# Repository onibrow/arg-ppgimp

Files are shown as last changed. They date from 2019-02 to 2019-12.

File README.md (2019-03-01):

# Arias Research Group - PPG & Impedence Measurement

## Seiya Ono Sp'19

The goal of this project is to collaborate with doctors at UCSD and Dr. Muller's student, Sina Faraji, to create a test bench for our group's Bioimpedence Array and OLED/OPD Oxymeter sensors to measure tissue damage in mice. We hope to use Sina Faraji's new OLED/OPD driver chip to take PPG measurements while using our own impedence arrays and electronics to measure tissue of the target.

-----

## Specs

- 1 PPG Sensor
    - 1 Red OLED
    - 1 NIR OLED
    - 1 OPD
    - Sina's Driver Chip
- 15 Impedence Electrodes
    - Impedence measurement AFE
    - Current Driver (200uA to 700uA, up to 1mA)
    - 15 to 2 selection mux
- 9V Power
- Coms over Serial

### PPG Sensor

Sina's OLED/OPD Driver Amplifier has the capability to driver 8 pairs of OLEDs and take readings from 8 OPDs. It handles all the amplification through SPI programmable registers. The closed loop in the transimpedence amplifiers can help get rid of any DC components in the OPD readings. It runs off of 1.1V digital logic, and 8V driver power.

If his chip does not go well, we will implement our own OLED drivers and OPD transimpedence amplifiers.

### Impedence Electrodes

We were asked to get our 15 electrode array to be able to take any impedence measurement between any two user selectable electrodes, while also being able to select any two electrodes to drive with a set amount of current. This divides this part of the board into three distance parts - the multiplexor selection and configuration, tunable current source, and impdence measurement. The following section will outline the different chip selection and their respective specs.

#### Multiplexor

Because the board is spec'd to be able to take impedence measurements as well as source current, it is critical to choose a multiplexor that has very low on resistance, while having very high off resistance. Luckily, most CMOS technology has this as standard, so picking an analog mux was not very difficult. We settled with the [ADG1608/1609](https://www.analog.com/en/products/adg1608.html) because of its 3 bit (8 input) mux, as well as its secondary variant 2 bit (4x2 input) DPDT (double pole double throw) configuration. To differentiate, the ADG1608 variant is the 3 bit 8 input mux, and the ADG1609 is the 2 bit 4x2 input mux. See the figure below for clarification.

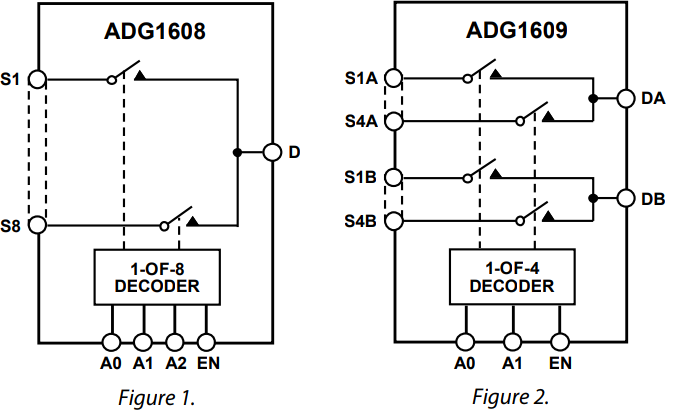
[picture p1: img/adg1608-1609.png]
mux diff


By using two pairs of ADG1608's, a 16x2 input 1x2 output can be created. This means the circuit can individually select a pair of electrodes to be used by the impedence analyzer and tunable current source. To select between either of the two inputs, the ADG1609 will be used as a demuxer to select either the impedence analyzer or tunable current source. The DPDT configuration is very usedful in this sceneario because we are trying to always drive a _pair_ of electrodes. Here are some important specs when running off of a 3.3V power rail.

| Parameter | Value | Unit |
| --------- | ----- | ---- |
| R\_on      | 13.5  | Ohms |
| S/D Leakage | 0.1 | nA max |
| -3dB 1608 | 34 | MHz typ |
| -3dB 1609 | 72 | MHz typ |
| C\_S OFF | 23 | pF typ |
| C\_D OFF 1608 | 145 | pF type |
| C\_D OFF 1609 | 72 | pF typ |
| C\_S/D ON 1608 | 173 | pF typ |
| C\_S/D ON 1609 | 95 | pF typ |
| I\_DD | 0.001 | uA typ |
| V\_DD | 3.3 | V |
|I\_S/D 1608 | 126 | mA max |
|I\_S/D 1609 | 94 | mA max |

As we are dealing with specimens in the 10K Ohm range, the 13.5 Ohm and 173pF ON impedence is negligible, even if the electrode is traveling through 2 multiplexors. The max available current draw is much over the required 1mA of current through the electrodes, so the chip fits our needs. It aslo fits our impedance chip bandwidth, where it can do frequency sweeps over 1kHz to 100kHz. More on this in the "Impedence Analyzer" section.

#### Tunable Current Source

In order to drive our selectable electrodes with a user defined amount of current, we needed an adjustable current source. For this task, the [LM134/LM234/LM334 3-Terminal Adjustable Current Source](http://www.ti.com/product/LM134) was chosen. Specifically, the LM334 was chosen for its small form factor and easily identifiable 3-Pin Through Hole casing. It has a huge operating voltage from 1V to 40V, and can be tuned to supply current between 1uA to 10mA. The chip can also be operated in a temperature compensation region to eliminate its temperature dependence up to 0.2% accuracy.

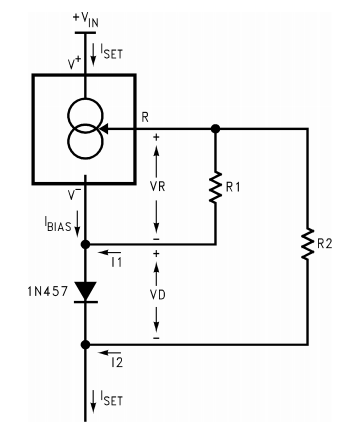
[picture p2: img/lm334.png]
LM334


For this circuit, the diode to use was already suggested, so the next choice was to pick out a digital potentiometer. TI also provided the math to prove the temperature coefficient compensation with the chosen diode, and drew the following relationship between R1 and R2:

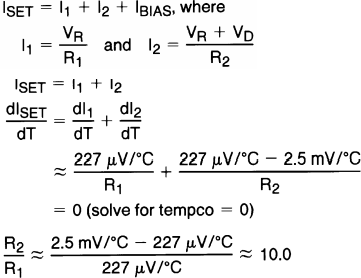
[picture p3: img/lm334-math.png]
lm334 math


From this, 1k and 10k 256 step digital potentiometers were chosen, with the math coming out to 3.9/39 Ohms per step, capable of driving in the range of 67.7uA to just short of 1mA. This just about fits our spec, going over to the upper limit of 1mA. The digital potentiometers chosen are the [AD8400](https://www.analog.com/en/products/ad8400.html) in both the 1K and 10K variant. They are controlled over SPI as designated write only slave devices. It can operate at between 3V and 5.5V and will typically draw less than 1mA.

#### Impedence Measurements

We would like to measure impedences between 1M Ohm (Magnitude) and 1k Ohm on our species. The chip for this is the [AD5933](https://www.analog.com/en/products/ad5933.html) which can do frequency sweeps. See Page 14 of the Data Sheet for more information on how to program the chip to do this.

Setting Gain - See Page 18 on how to choose the Gain setting resistor R\_FB to ensure that the analog readings do not saturate. The gain factor needs to be recalculated if R\_FB changes, if the output excitation voltage (more on this later) changes, or if the PGA gain is set differently. On the topic of operating voltages, there are 4 to choose from:

| Range | Output Excitation Voltage Amplitude | Output DC Bias Level | Output Series Resistance |
| ----- | ----------------------------------- | -------------------- | ------------------------ |
| 1 | 1.98 V p-p | 1.48 V | 200 Ohm |
| 2 | 0.97 V p-p | 0.76 V | 2.4k Ohm |
| 3 | 383 mV p-p | 0.31 V | 1.0k Ohm |
| 4 | 198 mV p-p | 0.173 V| 600 Ohm |

These numbers factor into what value should be chosen for the feedback resistor. The equation for choosing the feedback resistor is as follows:

Output Excitation Voltage Range * Gain Setting Resistor / Z\_Uknown * PGA Gain

By selecting the typical range 1 (~2V p-p) setting, we must choose a R\_FB that is roughly on the same order of magnitude as the unknown impedences we are measuring. From Yasser's Ulcer sensing paper (Swisher, S. L. et al. Impedance sensing device enables early detection of pressure ulcers in vivo. Nat. Commun. 6:6575 doi: 10.1038/ncomms7575 (2015)), we find that the typical impedence magnitude ranges from 10^4 to 10^6, so we will choos a 1M Ohm resistor for the feedback. This way, it should be able to cover a very wide range of impedences.

The chip does come with an internal 16.776 MHz oscillator, but it can be replaced by placing a 16MHz oscillator on MCLK, and then setting the control register to use the external clock. By default, on power up the internal oscillator is selected.

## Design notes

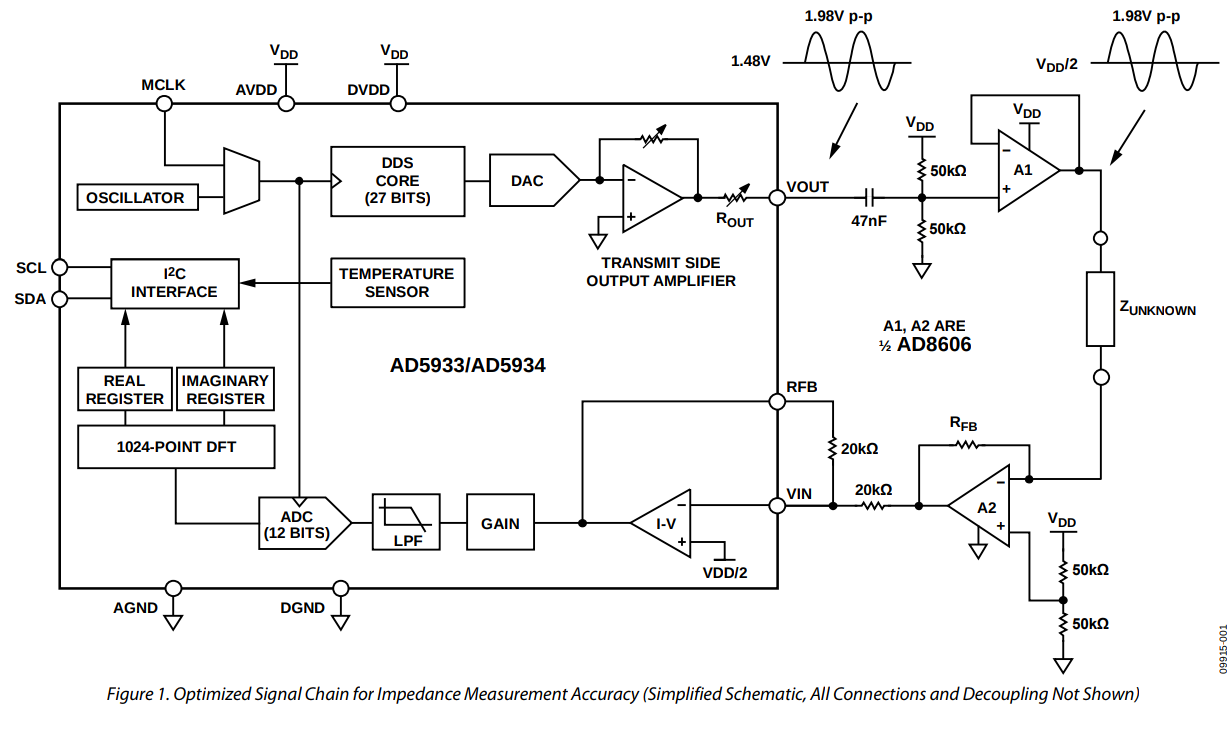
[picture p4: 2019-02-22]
img/ad5933-circ.png

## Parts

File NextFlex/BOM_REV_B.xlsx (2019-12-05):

Comment | Designator | Footprint | LCSC Part #（optional）
0.1uF | C9, C13, C14, C15 | 0603_C | C14663
1uF | C1, C2, C7, C8, C10, C11, C12 | 0603_C | C15849
18pF | C3, C4 | 0603_C | C1647
2.2uF | C5, C6 | 0603_C | C23630
10k | R1, R2, R3, R10 | 0603_R | C25804
22 | R4, R5 | 0603_R | C23345
330 | R7, R8, R11, R12, R13 | 0603_R | C23138
1k | R6, R9 | 0603_R | C21190
100k | R_CAL, R_FB | 0603_R | C25803
ATMEGA32U4 | U8 | QFN-44_EP_7x7x0.5P | C112161
Green | D3, D5 | LED_0603 | C72043
Red | D4, D7, D8, D9 | LED_0603 | C2286

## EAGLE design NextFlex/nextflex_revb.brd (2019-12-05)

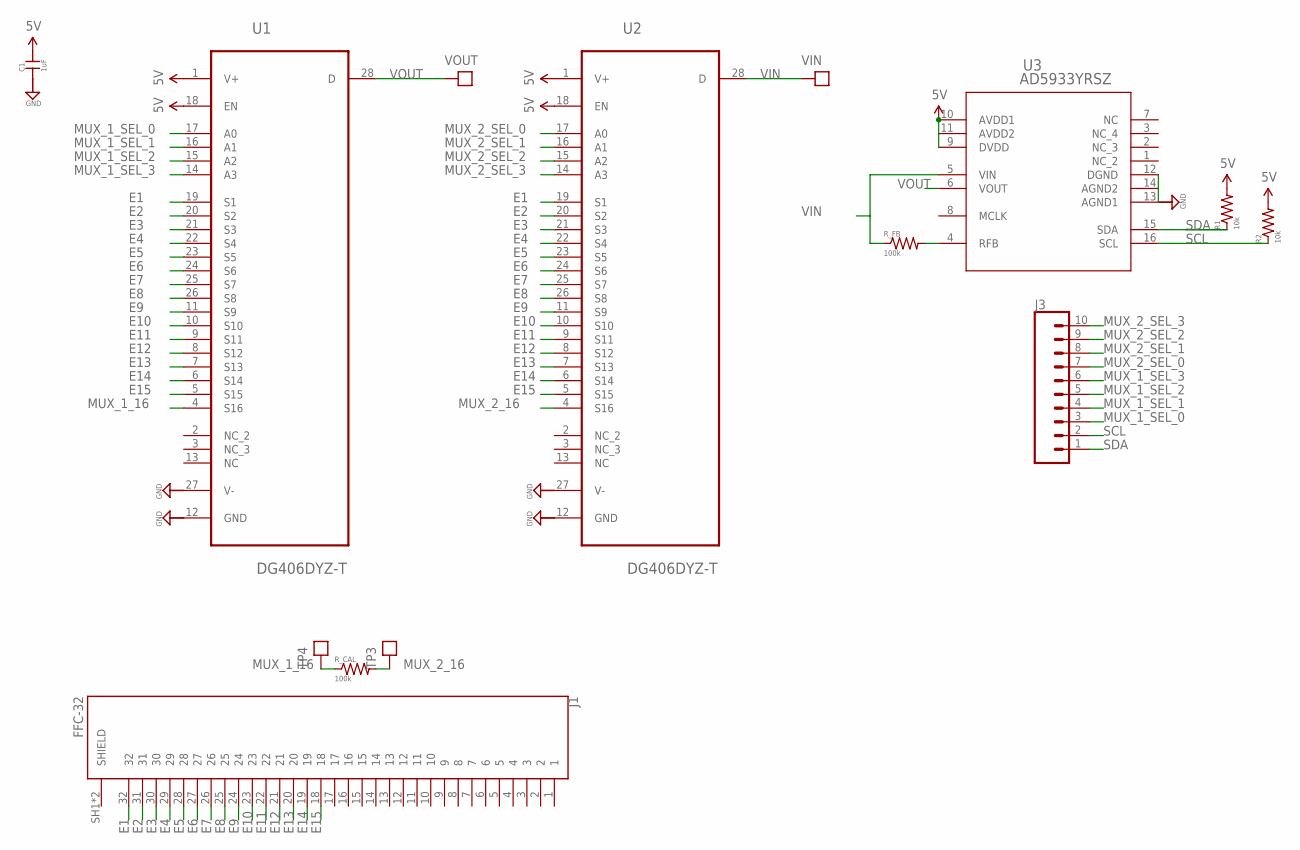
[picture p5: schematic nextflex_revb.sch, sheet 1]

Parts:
C1: 1uF; 0603-CAP
J1: FFC-32; MOLEX_503480-3200
J3: CONN_10"; 1X10
R1, R2: 10k; 0603-RES
R_CAL: 100k; 0603-RES
R_FB: 100k; 0603-RES
TP3, TP4: TEST_POINTTHRU; TEST_POINT
U1, U2: DG406DYZ-T; SOIC127P1032X265-28N
U3: AD5933YRSZ; RS_16
VIN: TEST_POINTTHRU; TEST_POINT
VOUT: TEST_POINTTHRU; TEST_POINT

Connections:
5V: C1.2, R1.2, R2.2, U1.1 (V+), U1.18 (EN), U2.1 (V+), U2.18 (EN), U3.9 (DVDD), U3.10 (AVDD1), U3.11 (AVDD2); also elsewhere on the board
E1: J1.32, U1.19 (S1), U2.19 (S1)
E2: J1.31, U1.20 (S2), U2.20 (S2)
E3: J1.30, U1.21 (S3), U2.21 (S3)
E4: J1.29, U1.22 (S4), U2.22 (S4)
E5: J1.28, U1.23 (S5), U2.23 (S5)
E6: J1.27, U1.24 (S6), U2.24 (S6)
E7: J1.26, U1.25 (S7), U2.25 (S7)
E8: J1.25, U1.26 (S8), U2.26 (S8)
E9: J1.24, U1.11 (S9), U2.11 (S9)
E10: J1.23, U1.10 (S10), U2.10 (S10)
E11: J1.22, U1.9 (S11), U2.9 (S11)
E12: J1.21, U1.8 (S12), U2.8 (S12)
E13: J1.20, U1.7 (S13), U2.7 (S13)
E14: J1.19, U1.6 (S14), U2.6 (S14)
E15: J1.18, U1.5 (S15), U2.5 (S15)
GND: C1.1, U1.12 (GND), U1.27 (V-), U2.12 (GND), U2.27 (V-), U3.12 (DGND), U3.13 (AGND1), U3.14 (AGND2); also elsewhere on the board
MUX_1_16: R_CAL.1, TP4.1, U1.4 (S16)
MUX_1_SEL_0: J3.3, U1.17 (A0); also elsewhere on the board
MUX_1_SEL_1: J3.4, U1.16 (A1); also elsewhere on the board
MUX_1_SEL_2: J3.5, U1.15 (A2); also elsewhere on the board
MUX_1_SEL_3: J3.6, U1.14 (A3); also elsewhere on the board
MUX_2_16: R_CAL.2, TP3.1, U2.4 (S16)
MUX_2_SEL_0: J3.7, U2.17 (A0); also elsewhere on the board
MUX_2_SEL_1: J3.8, U2.16 (A1); also elsewhere on the board
MUX_2_SEL_2: J3.9, U2.15 (A2); also elsewhere on the board
MUX_2_SEL_3: J3.10, U2.14 (A3); also elsewhere on the board
unnamed: R_FB.2, U3.4 (RFB)
SCL: J3.2, R2.1, U3.16 (SCL); also elsewhere on the board
SDA: J3.1, R1.1, U3.15 (SDA); also elsewhere on the board
VIN: R_FB.1, U2.28 (D), U3.5 (VIN), VIN.1
VOUT: U1.28 (D), U3.6 (VOUT), VOUT.1

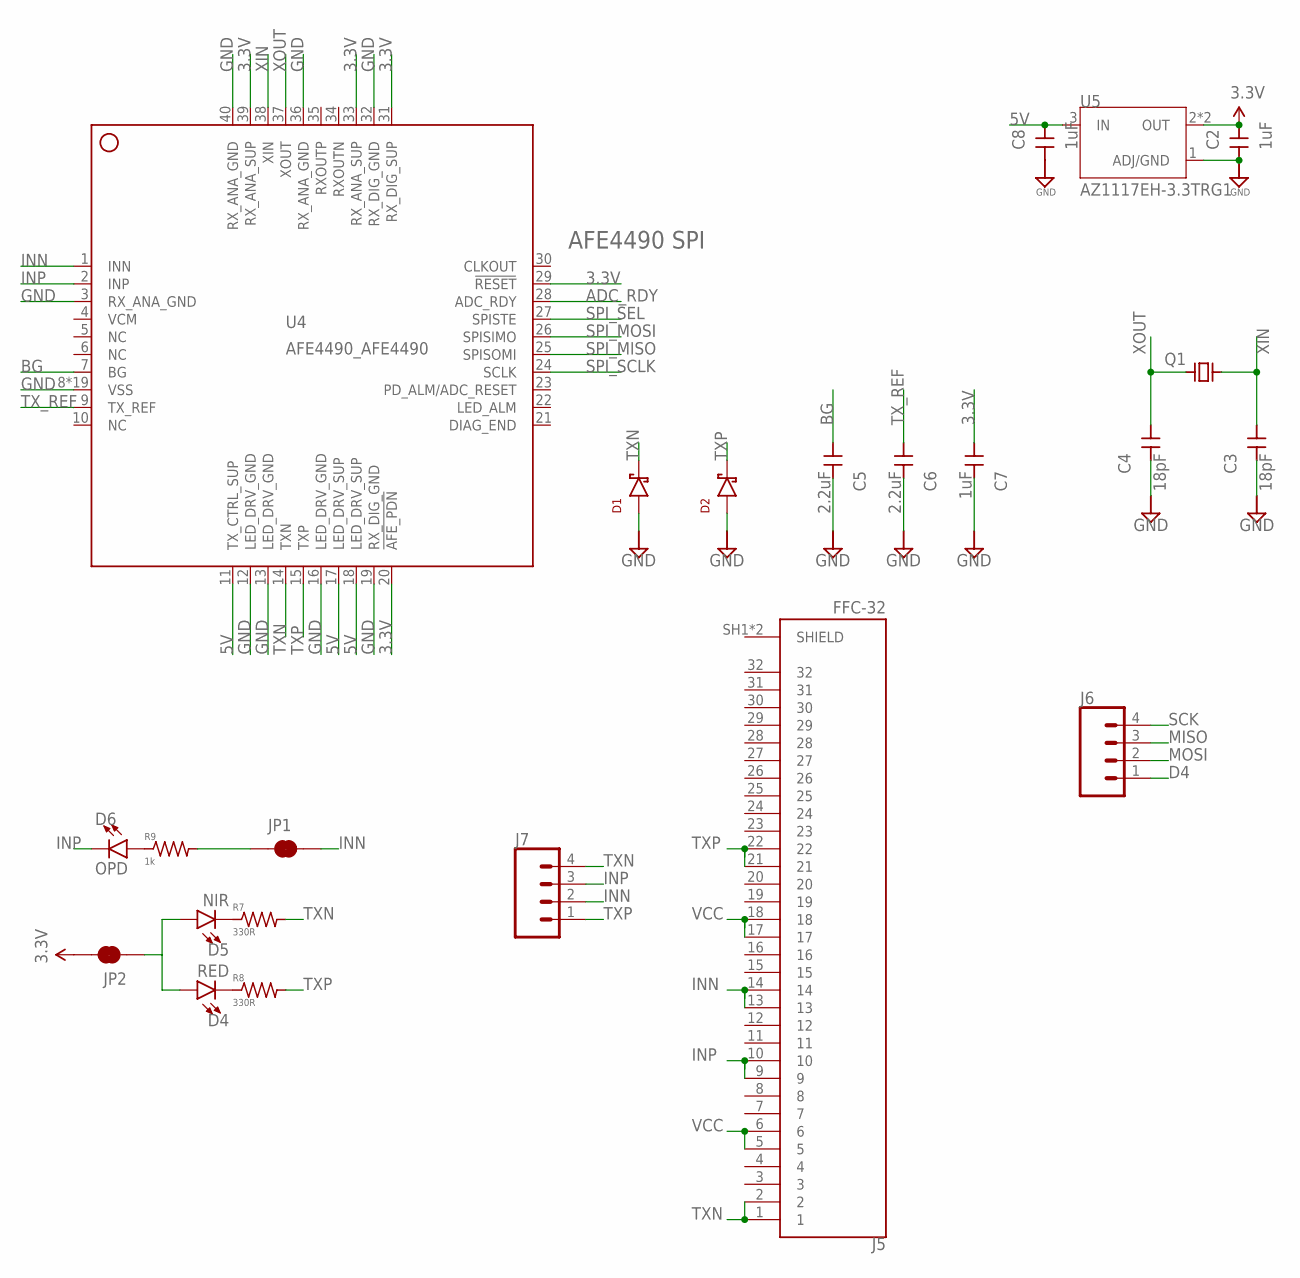
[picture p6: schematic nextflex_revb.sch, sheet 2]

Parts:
C2, C7, C8: 1uF; 0603-CAP
C3, C4: 18pF; 0603-CAP
C5, C6: 2.2uF; 0603-CAP
D1, D2: DIODE_CZRU; CZRU
D4: RED; LED-0603
D5: NIR; LED-0603
D6: OPD; LED-1206
J5: FFC-32; MOLEX_503480-3200
J6, J7: CONN_04; 1X04
JP1, JP2: JUMPER-SMT_2_NC_TRACE_NO-SILK; SMT-JUMPER_2_NC_TRACE_NO-SILK
Q1: CRYSTAL_SMOL; XTAL500X320X130N
R7, R8: 330R; 0603-RES
R9: 1k; 0603-RES
U4: AFE4490_AFE4490; AFE4490_QFN40-6X6
U5: AZ1117EH-3.3TRG1; SOT230P700X180-4N

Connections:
3.3V: C2.1, C7.1, JP2.2, U4.20 (!AFE_PDN), U4.29 (!RESET), U4.31 (RX_DIG_SUP), U4.33 (RX_ANA_SUP), U4.39 (RX_ANA_SUP), U5.2 (OUT), U5.4 (OUT); also elsewhere on the board
5V: C8.1, U4.11 (TX_CTRL_SUP), U4.17 (LED_DRV_SUP), U4.18 (LED_DRV_SUP), U5.3 (IN); also elsewhere on the board
ADC_RDY: U4.28 (ADC_RDY)
BG: C5.1, U4.7 (BG)
D4: J6.1; also elsewhere on the board
GND: C2.2, C3.2, C4.2, C5.2, C6.2, C7.2, C8.2, D1.P, D2.P, U4.3 (RX_ANA_GND), U4.8 (VSS), U4.12 (LED_DRV_GND), U4.13 (LED_DRV_GND), U4.16 (LED_DRV_GND), U4.19 (RX_DIG_GND), U4.32 (RX_DIG_GND), U4.36 (RX_ANA_GND), U4.40 (RX_ANA_GND), U4.EXP@1 (VSS), U4.EXP@2 (VSS), U4.EXP@3 (VSS), U4.EXP@4 (VSS), U4.EXP@5 (VSS), U4.EXP@6 (VSS), U4.EXP@7 (VSS), U4.EXP@8 (VSS), U4.EXP@9 (VSS), U4.EXP@10 (VSS), U4.EXP@11 (VSS), U4.EXP@12 (VSS), U4.EXP@13 (VSS), U4.EXP@14 (VSS), U4.EXP@15 (VSS), U4.EXP@16 (VSS), U4.PWR@1 (VSS), U4.PWR@2 (VSS), U5.1 (ADJ/GND); also elsewhere on the board
INN: J5.13, J5.14, J7.2, JP1.2, U4.1 (INN)
INP: D6.C, J5.9, J5.10, J7.3, U4.2 (INP)
MISO: J6.3; also elsewhere on the board
MOSI: J6.2; also elsewhere on the board
unnamed: D4.A, D5.A, JP2.1
unnamed: D5.C, R7.1
unnamed: D4.C, R8.1
unnamed: D6.A, R9.1
unnamed: JP1.1, R9.2
SCK: J6.4; also elsewhere on the board
SPI_MISO: U4.25 (SPISOMI); also elsewhere on the board
SPI_MOSI: U4.26 (SPISIMO); also elsewhere on the board
SPI_SCLK: U4.24 (SCLK); also elsewhere on the board
SPI_SEL: U4.27 (SPISTE); also elsewhere on the board
TXN: D1.N, J5.1, J5.2, J7.4, R7.2, U4.14 (TXN)
TXP: D2.N, J5.21, J5.22, J7.1, R8.2, U4.15 (TXP)
TX_REF: C6.1, U4.9 (TX_REF)
VCC: J5.5, J5.6, J5.17, J5.18; also elsewhere on the board
XIN: C3.1, Q1.1 (A), U4.38 (XIN)
XOUT: C4.1, Q1.2 (B), U4.37 (XOUT)

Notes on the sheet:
AFE4490 SPI

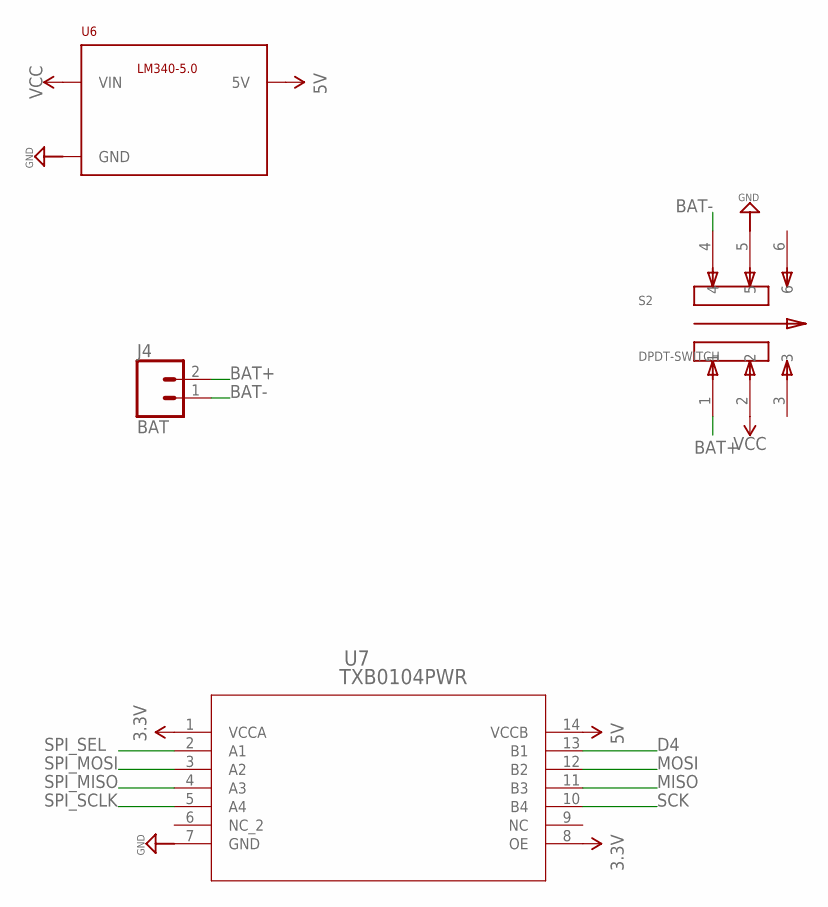
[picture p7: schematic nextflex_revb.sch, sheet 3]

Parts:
J4: BAT; 1X02
S2: DPDT-SWITCH; SW_JS202011SCQN
U6: LM340MPX-5.0230; SOT230P700X180-4N
U7: TXB0104PWR; PW14

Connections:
3.3V: U7.1 (VCCA), U7.8 (OE); also elsewhere on the board
5V: U6.3 (5V), U7.14 (VCCB); also elsewhere on the board
BAT+: J4.2, S2.1
BAT-: J4.1, S2.4
D4: U7.13 (B1); also elsewhere on the board
GND: S2.5, U6.2 (GND), U6.4 (GND), U7.7 (GND); also elsewhere on the board
MISO: U7.11 (B3); also elsewhere on the board
MOSI: U7.12 (B2); also elsewhere on the board
SCK: U7.10 (B4); also elsewhere on the board
SPI_MISO: U7.4 (A3); also elsewhere on the board
SPI_MOSI: U7.3 (A2); also elsewhere on the board
SPI_SCLK: U7.5 (A4); also elsewhere on the board
SPI_SEL: U7.2 (A1); also elsewhere on the board
VCC: S2.2, U6.1 (VIN); also elsewhere on the board

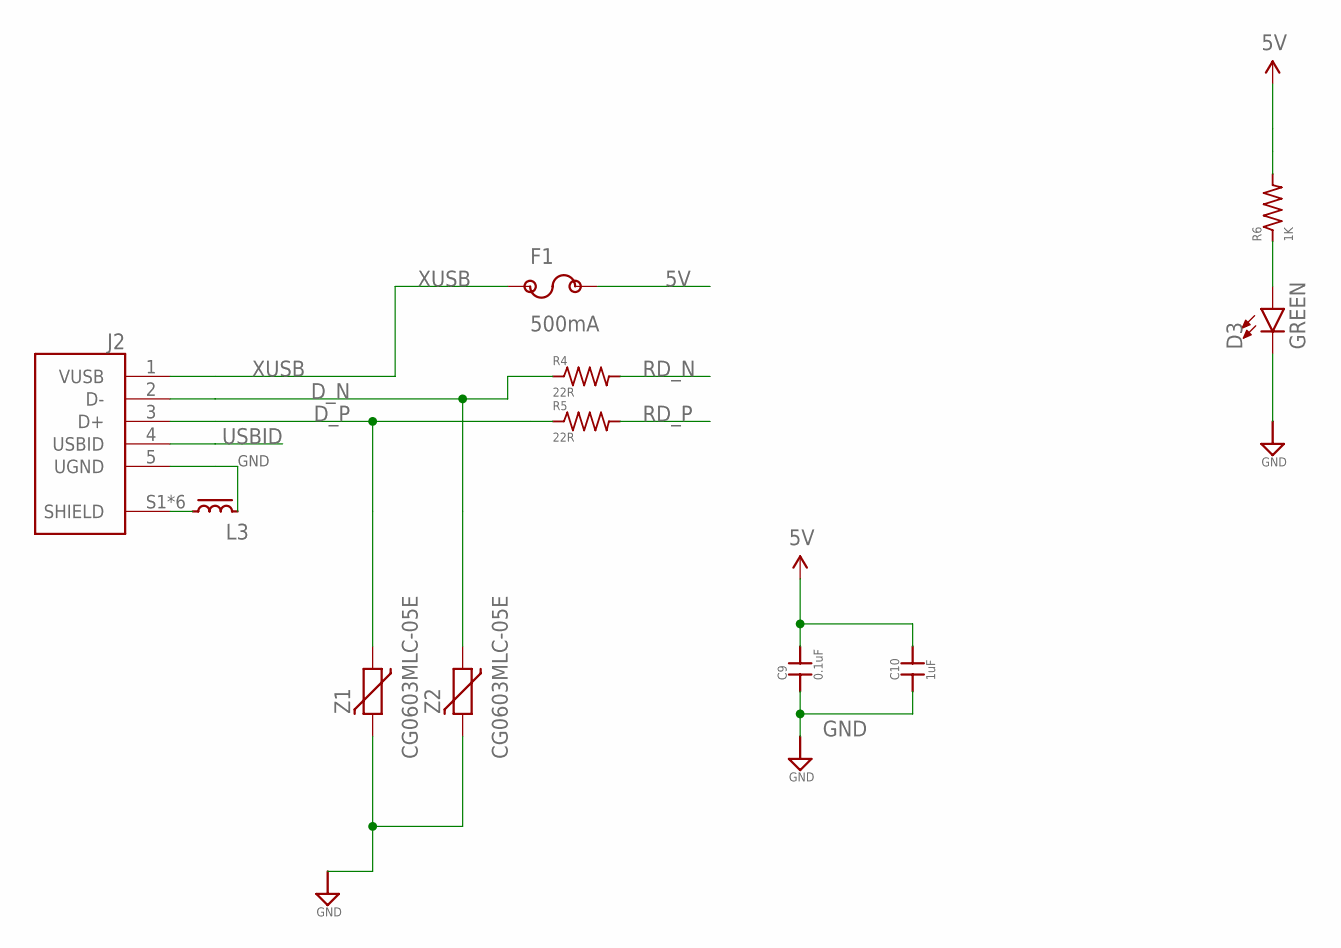
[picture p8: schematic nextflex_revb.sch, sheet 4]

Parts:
C9: 0.1uF; 0603-CAP
C10: 1uF; 0603-CAP
D3: GREEN; LED-0603
F1: 500mA; 1206
J2: USB; FCI_10103594-0001LF
L3: IND; IND_2012
R4, R5: 22R; 0603-RES
R6: 1K; 0603-RES
Z1, Z2: CG0603MLC-05E; 0603-RES

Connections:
5V: C9.2, C10.2, F1.2, R6.2; also elsewhere on the board
D_N: J2.2 (D-), R4.1, Z2.1
D_P: J2.3 (D+), R5.1, Z1.1
GND: C9.1, C10.1, D3.C, J2.5 (UGND), L3.2, Z1.2, Z2.2; also elsewhere on the board
unnamed: D3.A, R6.1
RD_N: R4.2; also elsewhere on the board
RD_P: R5.2; also elsewhere on the board
SHIELD: J2.S1 (SHIELD), J2.S2 (SHIELD), J2.S3 (SHIELD), J2.S4 (SHIELD), J2.S5 (SHIELD), J2.S6 (SHIELD), L3.1
USBID: J2.4 (USBID)
XUSB: F1.1, J2.1 (VUSB)

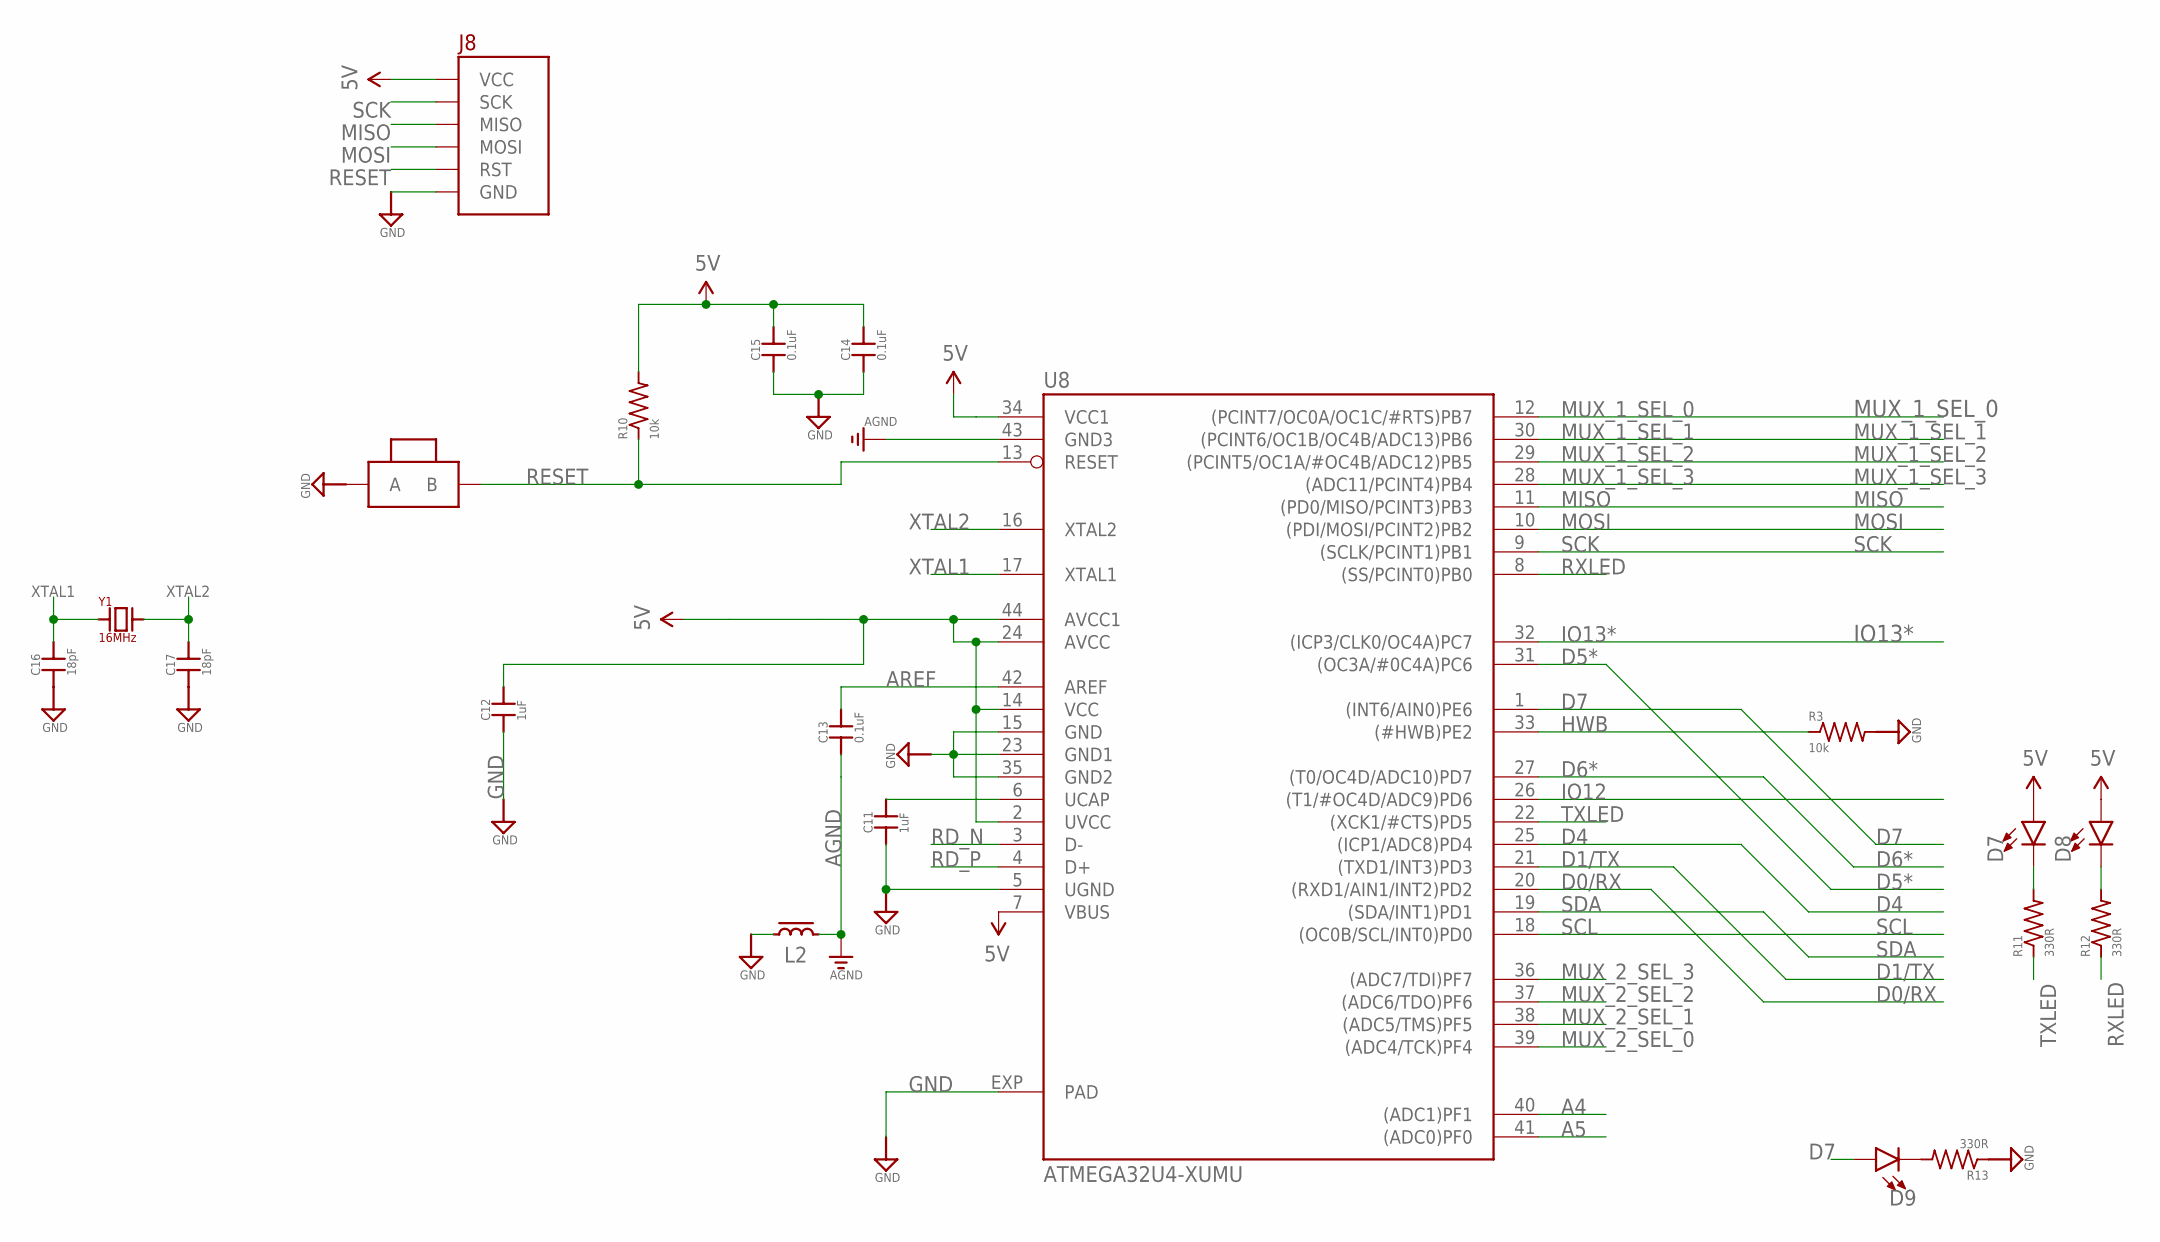
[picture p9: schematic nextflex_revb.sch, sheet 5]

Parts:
C11, C12: 1uF; 0603-CAP
C13, C14, C15: 0.1uF; 0603-CAP
C16, C17: 18pF; 0603-CAP
D7, D8, D9: LED0603; LED-0603
J8: BURNIN
L2: IND; IND_2012
R3, R10: 10k; 0603-RES
R11, R12, R13: 330R; 0603-RES
SW1: BTN-PTS810; BTN_PTS810
U8: ATMEGA32U4-XUMU; QFN44ML7X7
Y1: 16MHz; XTAL500X320X130N

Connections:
5V: C12.2, C14.2, C15.2, D7.A, D8.A, J8.3.3V (VCC), R10.2, U8.2 (UVCC), U8.7 (VBUS), U8.14 (VCC), U8.24 (AVCC), U8.34 (VCC1), U8.44 (AVCC1); also elsewhere on the board
A4: U8.40 ((ADC1)PF1)
A5: U8.41 ((ADC0)PF0)
AGND: C13.1, L2.2, U8.43 (GND3)
AREF: C13.2, U8.42 (AREF)
D0/RX: U8.20 ((RXD1/AIN1/INT2)PD2)
D1/TX: U8.21 ((TXD1/INT3)PD3)
D4: U8.25 ((ICP1/ADC8)PD4); also elsewhere on the board
D5*: U8.31 ((OC3A/#0C4A)PC6)
D6*: U8.27 ((T0/OC4D/ADC10)PD7)
D7: D9.A, U8.1 ((INT6/AIN0)PE6)
GND: C11.1, C12.1, C14.1, C15.1, C16.1, C17.1, J8.GND, L2.1, R3.2, R13.1, SW1.1 (A), SW1.2 (A), U8.5 (UGND), U8.15 (GND), U8.23 (GND1), U8.35 (GND2), U8.EXP (PAD); also elsewhere on the board
HWB: R3.1, U8.33 ((#HWB)PE2)
IO12: U8.26 ((T1/#OC4D/ADC9)PD6)
IO13*: U8.32 ((ICP3/CLK0/OC4A)PC7)
MISO: J8.MISO, U8.11 ((PD0/MISO/PCINT3)PB3); also elsewhere on the board
MOSI: J8.MOSI, U8.10 ((PDI/MOSI/PCINT2)PB2); also elsewhere on the board
MUX_1_SEL_0: U8.12 ((PCINT7/OC0A/OC1C/#RTS)PB7); also elsewhere on the board
MUX_1_SEL_1: U8.30 ((PCINT6/OC1B/OC4B/ADC13)PB6); also elsewhere on the board
MUX_1_SEL_2: U8.29 ((PCINT5/OC1A/#OC4B/ADC12)PB5); also elsewhere on the board
MUX_1_SEL_3: U8.28 ((ADC11/PCINT4)PB4); also elsewhere on the board
MUX_2_SEL_0: U8.39 ((ADC4/TCK)PF4); also elsewhere on the board
MUX_2_SEL_1: U8.38 ((ADC5/TMS)PF5); also elsewhere on the board
MUX_2_SEL_2: U8.37 ((ADC6/TDO)PF6); also elsewhere on the board
MUX_2_SEL_3: U8.36 ((ADC7/TDI)PF7); also elsewhere on the board
unnamed: D7.C, R11.2
unnamed: D8.C, R12.2
unnamed: D9.C, R13.2
RD_N: U8.3 (D-); also elsewhere on the board
RD_P: U8.4 (D+); also elsewhere on the board
RESET: J8.RST, R10.1, SW1.3 (B), SW1.4 (B), U8.13 (RESET)
RXLED: R12.1, U8.8 ((SS/PCINT0)PB0)
SCK: J8.SCK, U8.9 ((SCLK/PCINT1)PB1); also elsewhere on the board
SCL: U8.18 ((OC0B/SCL/INT0)PD0); also elsewhere on the board
SDA: U8.19 ((SDA/INT1)PD1); also elsewhere on the board
TXLED: R11.1, U8.22 ((XCK1/#CTS)PD5)
UCAP: C11.2, U8.6 (UCAP)
XTAL1: C16.2, U8.17 (XTAL1), Y1.1 (A)
XTAL2: C17.2, U8.16 (XTAL2), Y1.2 (B)

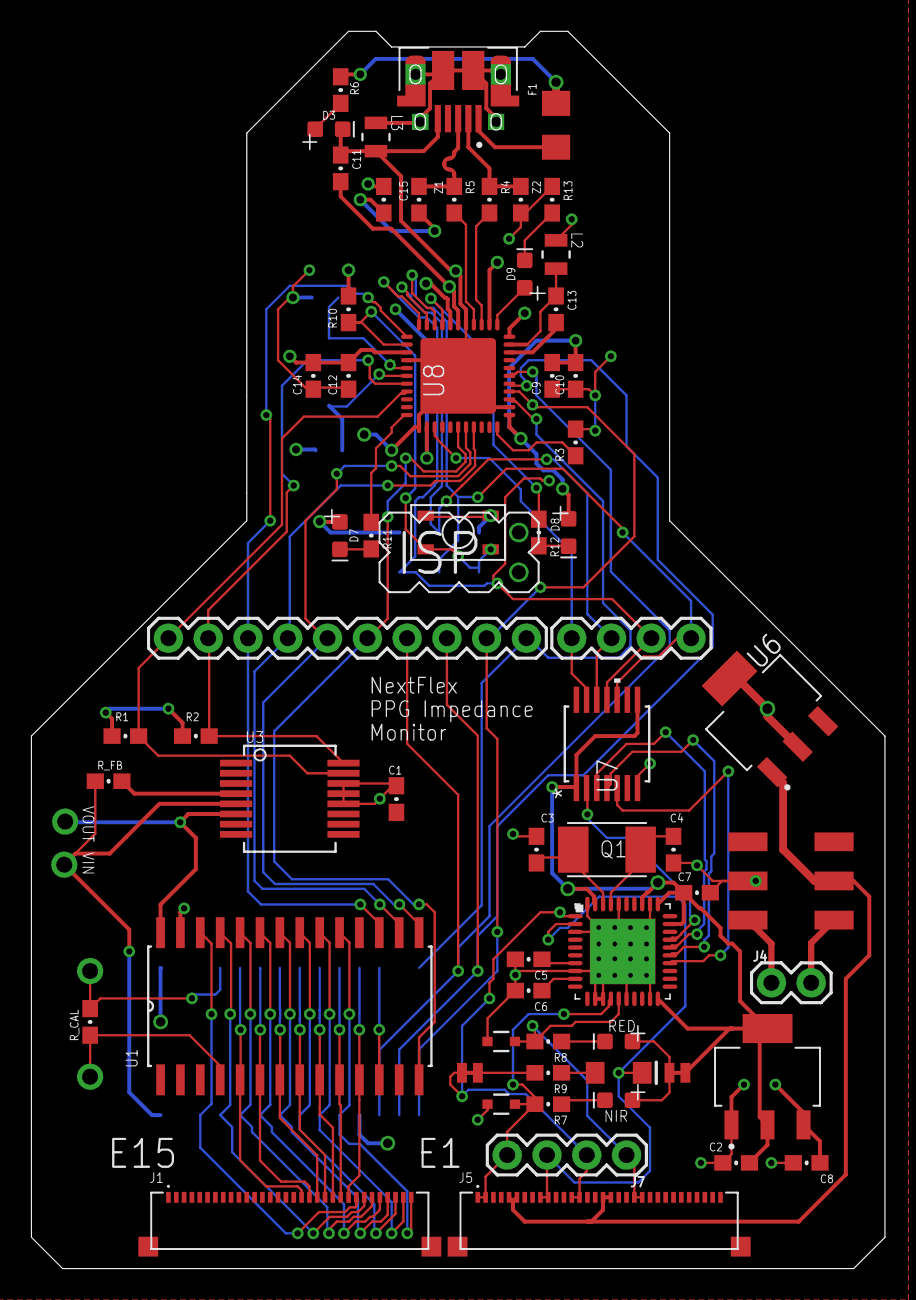
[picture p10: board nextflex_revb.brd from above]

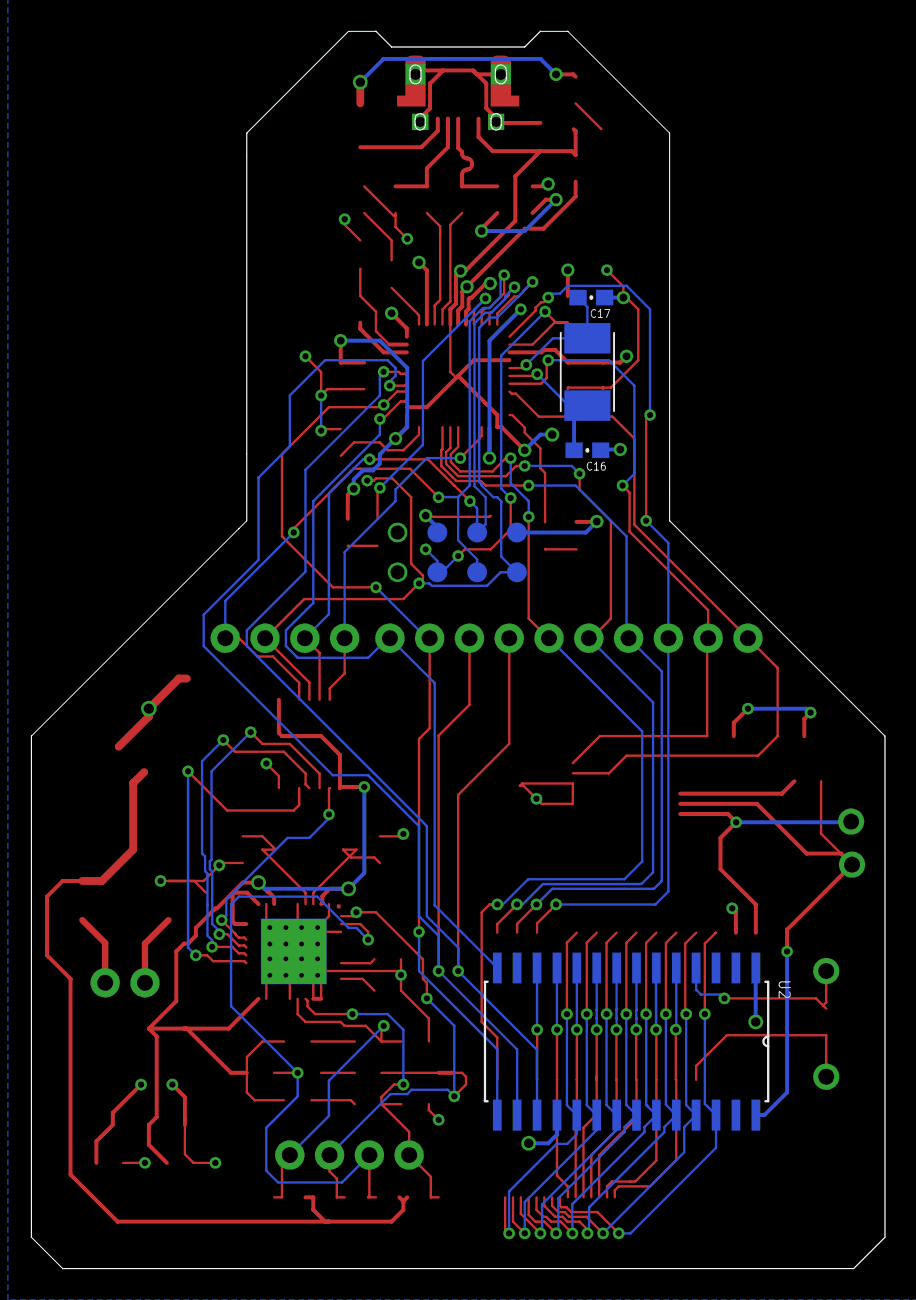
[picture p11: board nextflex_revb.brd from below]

Board: 2 copper layers, 54.5 x 79.0 mm, 72 parts (4 on the bottom side), 77 nets.

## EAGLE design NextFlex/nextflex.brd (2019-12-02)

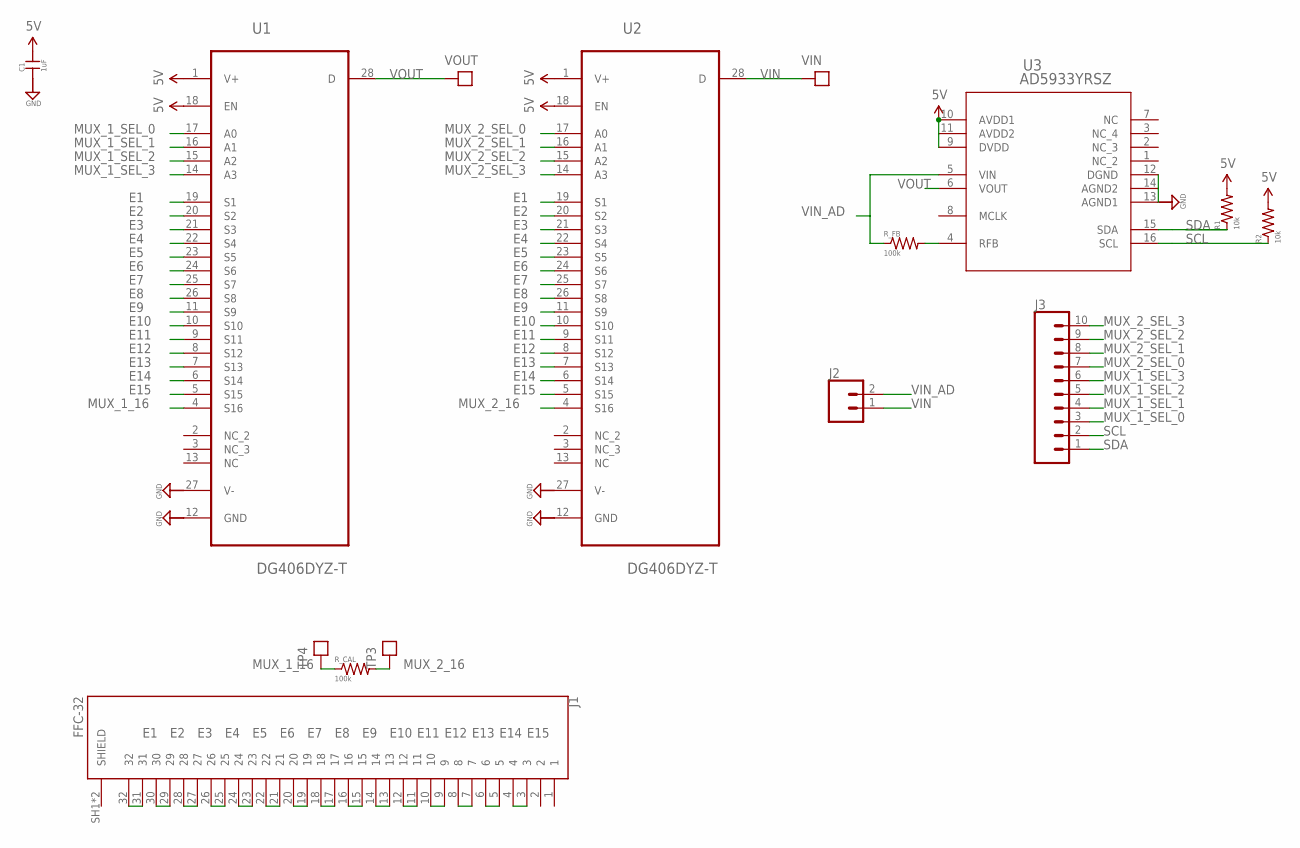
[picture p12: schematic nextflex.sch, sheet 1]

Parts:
C1: 1uF; 0603-CAP
J1: FFC-32; MOLEX_503480-3200
J2: CONN_02; 1X02
J3: CONN_10"; 1X10
R1, R2: 10k; 0603-RES
R_CAL: 100k; 0603-RES
R_FB: 100k; 0603-RES
TP3, TP4: TEST_POINTTHRU; TEST_POINT
U1, U2: DG406DYZ-T; SOIC127P1032X265-28N
U3: AD5933YRSZ; RS_16
VIN: TEST_POINTTHRU; TEST_POINT
VOUT: TEST_POINTTHRU; TEST_POINT

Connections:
5V: C1.2, R1.2, R2.2, U1.1 (V+), U1.18 (EN), U2.1 (V+), U2.18 (EN), U3.9 (DVDD), U3.10 (AVDD1), U3.11 (AVDD2); also elsewhere on the board
E1: J1.31, J1.32, U1.19 (S1), U2.19 (S1)
E2: J1.29, J1.30, U1.20 (S2), U2.20 (S2)
E3: J1.27, J1.28, U1.21 (S3), U2.21 (S3)
E4: J1.25, J1.26, U1.22 (S4), U2.22 (S4)
E5: J1.23, J1.24, U1.23 (S5), U2.23 (S5)
E6: J1.21, J1.22, U1.24 (S6), U2.24 (S6)
E7: J1.19, J1.20, U1.25 (S7), U2.25 (S7)
E8: J1.17, J1.18, U1.26 (S8), U2.26 (S8)
E9: J1.15, J1.16, U1.11 (S9), U2.11 (S9)
E10: J1.13, J1.14, U1.10 (S10), U2.10 (S10)
E11: J1.11, J1.12, U1.9 (S11), U2.9 (S11)
E12: J1.9, J1.10, U1.8 (S12), U2.8 (S12)
E13: J1.7, J1.8, U1.7 (S13), U2.7 (S13)
E14: J1.5, J1.6, U1.6 (S14), U2.6 (S14)
E15: J1.3, J1.4, U1.5 (S15), U2.5 (S15)
GND: C1.1, U1.12 (GND), U1.27 (V-), U2.12 (GND), U2.27 (V-), U3.12 (DGND), U3.13 (AGND1), U3.14 (AGND2); also elsewhere on the board
MUX_1_16: R_CAL.1, TP4.1, U1.4 (S16)
MUX_1_SEL_0: J3.3, U1.17 (A0)
MUX_1_SEL_1: J3.4, U1.16 (A1)
MUX_1_SEL_2: J3.5, U1.15 (A2)
MUX_1_SEL_3: J3.6, U1.14 (A3)
MUX_2_16: R_CAL.2, TP3.1, U2.4 (S16)
MUX_2_SEL_0: J3.7, U2.17 (A0)
MUX_2_SEL_1: J3.8, U2.16 (A1)
MUX_2_SEL_2: J3.9, U2.15 (A2)
MUX_2_SEL_3: J3.10, U2.14 (A3)
unnamed: R_FB.2, U3.4 (RFB)
SCL: J3.2, R2.1, U3.16 (SCL)
SDA: J3.1, R1.1, U3.15 (SDA)
VIN: J2.1, U2.28 (D), VIN.1
VIN_AD: J2.2, R_FB.1, U3.5 (VIN)
VOUT: U1.28 (D), U3.6 (VOUT), VOUT.1

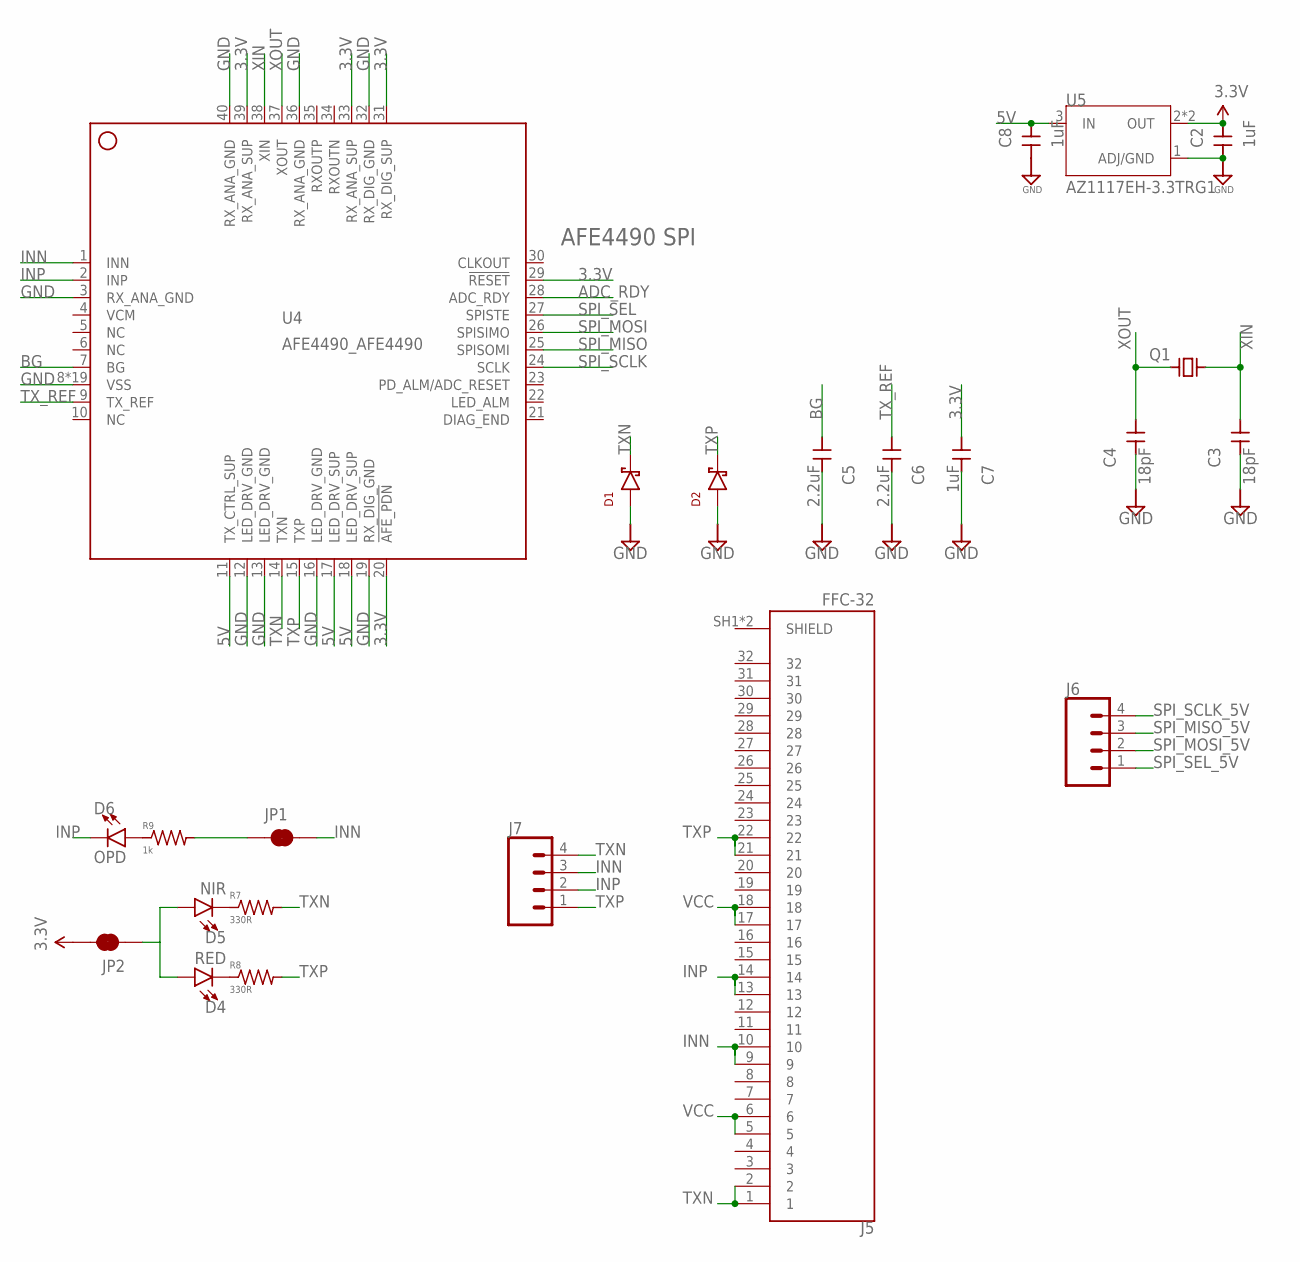
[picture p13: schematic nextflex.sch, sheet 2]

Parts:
C2, C7, C8: 1uF; 0603-CAP
C3, C4: 18pF; 0603-CAP
C5, C6: 2.2uF; 0603-CAP
D1, D2: DIODE_CZRU; CZRU
D4: RED; LED-0603
D5: NIR; LED-0603
D6: OPD; LED-1206
J5: FFC-32; MOLEX_503480-3200
J6, J7: CONN_04; 1X04
JP1, JP2: JUMPER-SMT_2_NC_TRACE_NO-SILK; SMT-JUMPER_2_NC_TRACE_NO-SILK
Q1: CRYSTAL_SMOL; XTAL500X320X130N
R7, R8: 330R; 0603-RES
R9: 1k; 0603-RES
U4: AFE4490_AFE4490; AFE4490_QFN40-6X6
U5: AZ1117EH-3.3TRG1; SOT230P700X180-4N

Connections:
3.3V: C2.1, C7.1, JP2.2, U4.20 (!AFE_PDN), U4.29 (!RESET), U4.31 (RX_DIG_SUP), U4.33 (RX_ANA_SUP), U4.39 (RX_ANA_SUP), U5.2 (OUT), U5.4 (OUT); also elsewhere on the board
5V: C8.1, U4.11 (TX_CTRL_SUP), U4.17 (LED_DRV_SUP), U4.18 (LED_DRV_SUP), U5.3 (IN); also elsewhere on the board
ADC_RDY: U4.28 (ADC_RDY)
BG: C5.1, U4.7 (BG)
GND: C2.2, C3.2, C4.2, C5.2, C6.2, C7.2, C8.2, D1.P, D2.P, U4.3 (RX_ANA_GND), U4.8 (VSS), U4.12 (LED_DRV_GND), U4.13 (LED_DRV_GND), U4.16 (LED_DRV_GND), U4.19 (RX_DIG_GND), U4.32 (RX_DIG_GND), U4.36 (RX_ANA_GND), U4.40 (RX_ANA_GND), U4.EXP@1 (VSS), U4.EXP@2 (VSS), U4.EXP@3 (VSS), U4.EXP@4 (VSS), U4.EXP@5 (VSS), U4.EXP@6 (VSS), U4.EXP@7 (VSS), U4.EXP@8 (VSS), U4.EXP@9 (VSS), U4.EXP@10 (VSS), U4.EXP@11 (VSS), U4.EXP@12 (VSS), U4.EXP@13 (VSS), U4.EXP@14 (VSS), U4.EXP@15 (VSS), U4.EXP@16 (VSS), U4.PWR@1 (VSS), U4.PWR@2 (VSS), U5.1 (ADJ/GND); also elsewhere on the board
INN: J5.9, J5.10, J7.3, JP1.2, U4.1 (INN)
INP: D6.C, J5.13, J5.14, J7.2, U4.2 (INP)
unnamed: D4.A, D5.A, JP2.1
unnamed: D5.C, R7.1
unnamed: D4.C, R8.1
unnamed: D6.A, R9.1
unnamed: JP1.1, R9.2
SPI_MISO: U4.25 (SPISOMI); also elsewhere on the board
SPI_MISO_5V: J6.3; also elsewhere on the board
SPI_MOSI: U4.26 (SPISIMO); also elsewhere on the board
SPI_MOSI_5V: J6.2; also elsewhere on the board
SPI_SCLK: U4.24 (SCLK); also elsewhere on the board
SPI_SCLK_5V: J6.4; also elsewhere on the board
SPI_SEL: U4.27 (SPISTE); also elsewhere on the board
SPI_SEL_5V: J6.1; also elsewhere on the board
TXN: D1.N, J5.1, J5.2, J7.4, R7.2, U4.14 (TXN)
TXP: D2.N, J5.21, J5.22, J7.1, R8.2, U4.15 (TXP)
TX_REF: C6.1, U4.9 (TX_REF)
VCC: J5.5, J5.6, J5.17, J5.18; also elsewhere on the board
XIN: C3.1, Q1.1 (A), U4.38 (XIN)
XOUT: C4.1, Q1.2 (B), U4.37 (XOUT)

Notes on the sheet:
AFE4490 SPI

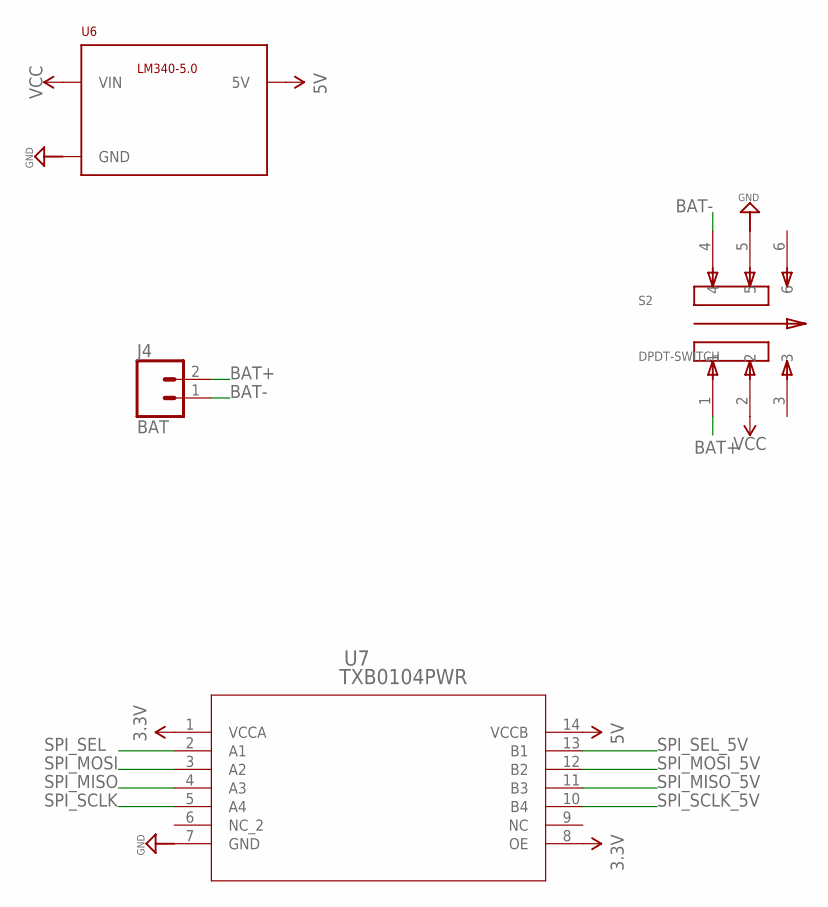
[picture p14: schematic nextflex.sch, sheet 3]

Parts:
J4: BAT; 1X02
S2: DPDT-SWITCH; SW_JS202011SCQN
U6: LM340MPX-5.0230; SOT230P700X180-4N
U7: TXB0104PWR; PW14

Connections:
3.3V: U7.1 (VCCA), U7.8 (OE); also elsewhere on the board
5V: U6.3 (5V), U7.14 (VCCB); also elsewhere on the board
BAT+: J4.2, S2.1
BAT-: J4.1, S2.4
GND: S2.5, U6.2 (GND), U6.4 (GND), U7.7 (GND); also elsewhere on the board
SPI_MISO: U7.4 (A3); also elsewhere on the board
SPI_MISO_5V: U7.11 (B3); also elsewhere on the board
SPI_MOSI: U7.3 (A2); also elsewhere on the board
SPI_MOSI_5V: U7.12 (B2); also elsewhere on the board
SPI_SCLK: U7.5 (A4); also elsewhere on the board
SPI_SCLK_5V: U7.10 (B4); also elsewhere on the board
SPI_SEL: U7.2 (A1); also elsewhere on the board
SPI_SEL_5V: U7.13 (B1); also elsewhere on the board
VCC: S2.2, U6.1 (VIN); also elsewhere on the board

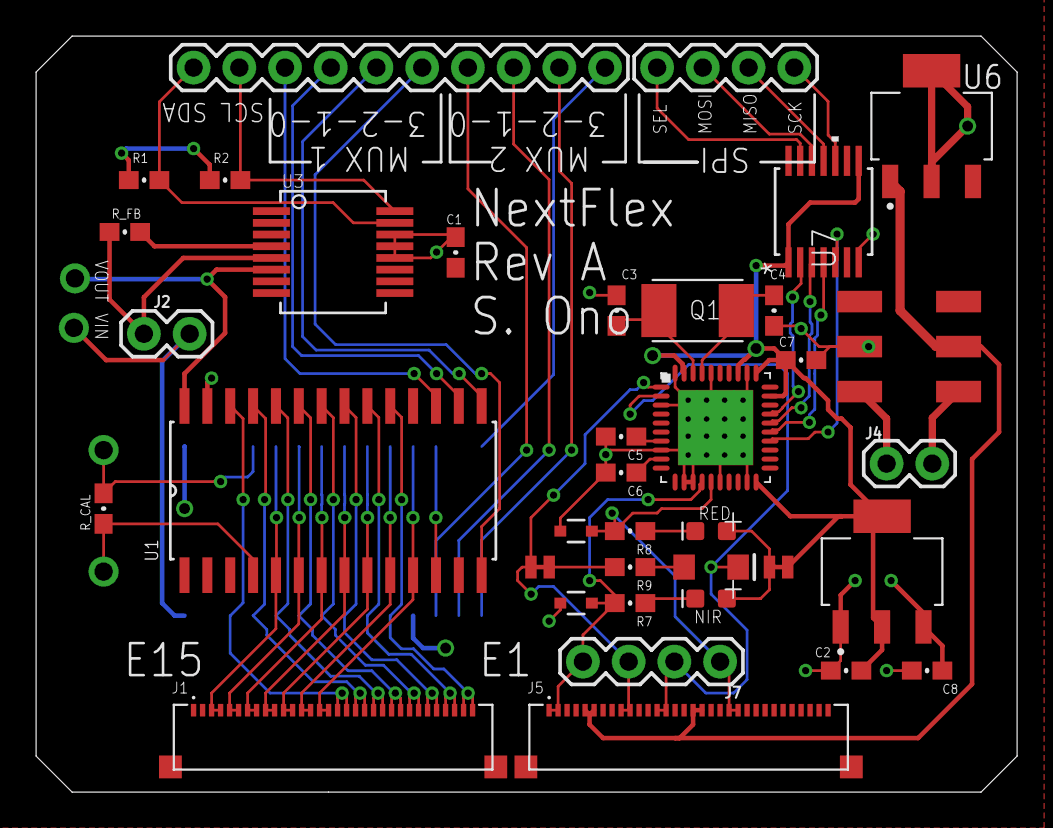
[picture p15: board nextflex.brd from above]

Board: 2 copper layers, 54.5 x 42.0 mm, 42 parts (1 on the bottom side), 58 nets.

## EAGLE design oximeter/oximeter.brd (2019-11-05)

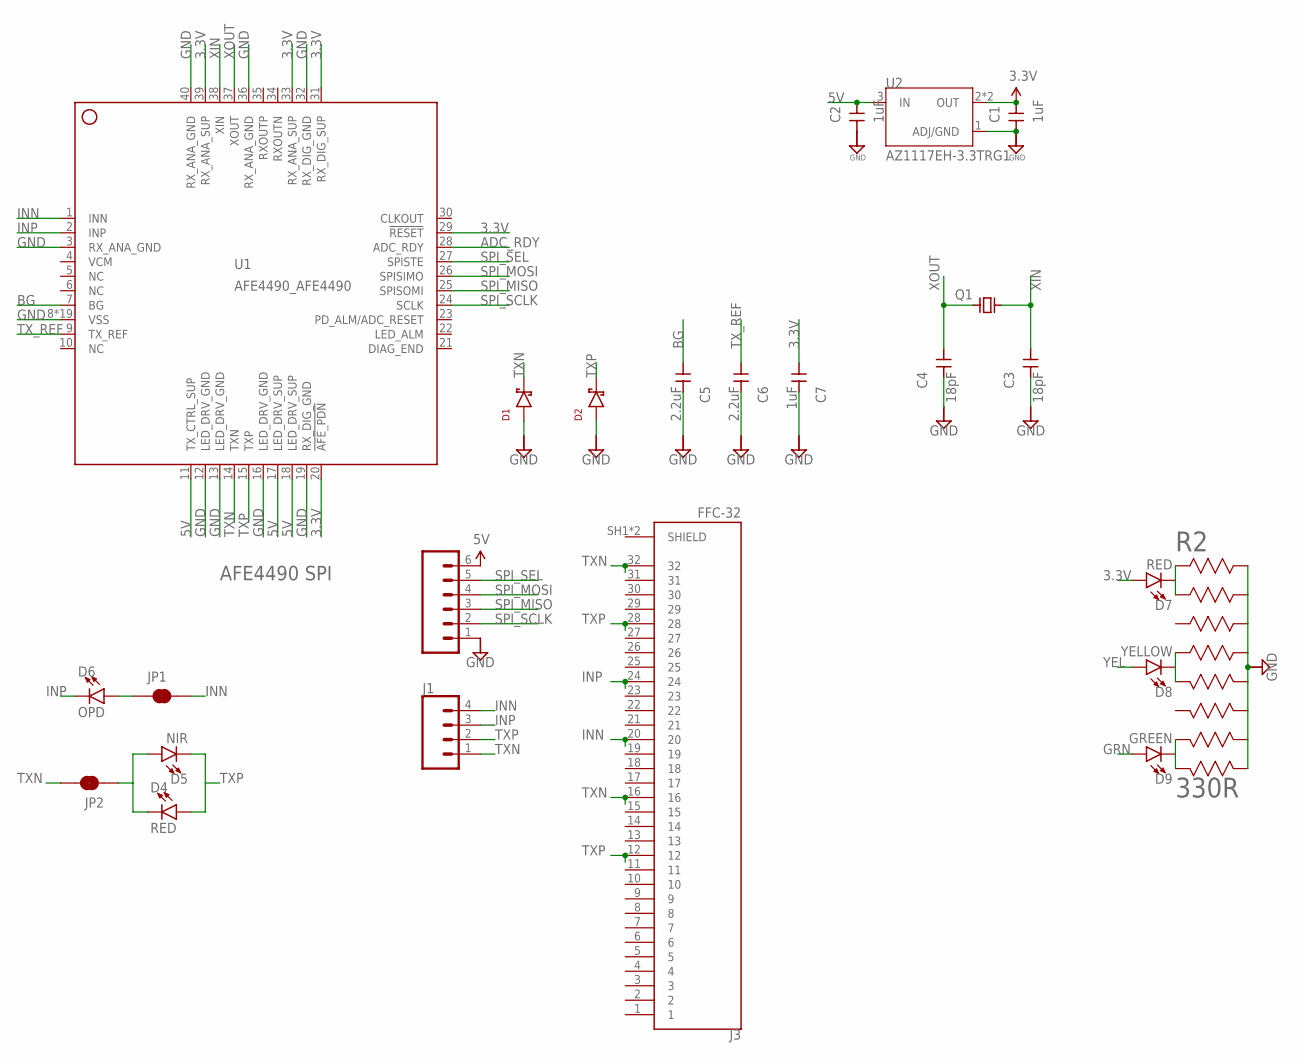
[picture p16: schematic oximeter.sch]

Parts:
C1, C2, C7: 1uF; 0603-CAP
C3, C4: 18pF; 0603-CAP
C5, C6: 2.2uF; 0603-CAP
D1, D2: DIODE_CZRU; CZRU
D4, D7: RED; LED-0603
D5: NIR; LED-0603
D6: OPD; LED-1206
D8: YELLOW; LED-0603
D9: GREEN; LED-0603
J1: CONN_04; 1X04
J2: CONN_06SILK_FEMALE_PTH; 1X06
J3: FFC-32; MOLEX_503480-3200
JP1, JP2: JUMPER-SMT_2_NC_TRACE_NO-SILK; SMT-JUMPER_2_NC_TRACE_NO-SILK
Q1: CRYSTAL_ECS_8MHZ; XTAL_ECS-80-18-5PX-TR
R2: 330R; EXB2HV
U1: AFE4490_AFE4490; AFE4490_QFN40-6X6
U2: AZ1117EH-3.3TRG1; SOT230P700X180-4N

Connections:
3.3V: C1.1, C7.1, D7.A, U1.20 (!AFE_PDN), U1.29 (!RESET), U1.31 (RX_DIG_SUP), U1.33 (RX_ANA_SUP), U1.39 (RX_ANA_SUP), U2.2 (OUT), U2.4 (OUT)
5V: C2.1, J2.6, U1.11 (TX_CTRL_SUP), U1.17 (LED_DRV_SUP), U1.18 (LED_DRV_SUP), U2.3 (IN)
ADC_RDY: U1.28 (ADC_RDY)
BG: C5.1, U1.7 (BG)
GND: C1.2, C2.2, C3.2, C4.2, C5.2, C6.2, C7.2, D1.P, D2.P, J2.1, R2.9, R2.10, R2.11, R2.12, R2.13, R2.14, R2.15, R2.16, U1.3 (RX_ANA_GND), U1.8 (VSS), U1.12 (LED_DRV_GND), U1.13 (LED_DRV_GND), U1.16 (LED_DRV_GND), U1.19 (RX_DIG_GND), U1.32 (RX_DIG_GND), U1.36 (RX_ANA_GND), U1.40 (RX_ANA_GND), U1.EXP@1 (VSS), U1.EXP@2 (VSS), U1.EXP@3 (VSS), U1.EXP@4 (VSS), U1.EXP@5 (VSS), U1.EXP@6 (VSS), U1.EXP@7 (VSS), U1.EXP@8 (VSS), U1.EXP@9 (VSS), U1.EXP@10 (VSS), U1.EXP@11 (VSS), U1.EXP@12 (VSS), U1.EXP@13 (VSS), U1.EXP@14 (VSS), U1.EXP@15 (VSS), U1.EXP@16 (VSS), U1.PWR@1 (VSS), U1.PWR@2 (VSS), U2.1 (ADJ/GND)
GRN: D9.A
INN: J1.4, J3.20, JP1.2, U1.1 (INN)
INN_BUF: D6.A, JP1.1
INP: D6.C, J1.3, J3.24, U1.2 (INP)
unnamed: D7.C, R2.1, R2.2
unnamed: D8.C, R2.4, R2.5
unnamed: D9.C, R2.7, R2.8
SPI_MISO: J2.3, U1.25 (SPISOMI)
SPI_MOSI: J2.4, U1.26 (SPISIMO)
SPI_SCLK: J2.2, U1.24 (SCLK)
SPI_SEL: J2.5, U1.27 (SPISTE)
TXN: D1.N, J1.1, J3.16, J3.32, JP2.2, U1.14 (TXN)
TXN_BUF: D4.C, D5.A, JP2.1
TXP: D2.N, D4.A, D5.C, J1.2, J3.12, J3.28, U1.15 (TXP)
TX_REF: C6.1, U1.9 (TX_REF)
XIN: C3.1, Q1.1 (A), U1.38 (XIN)
XOUT: C4.1, Q1.2 (B), U1.37 (XOUT)
YEL: D8.A

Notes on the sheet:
AFE4490 SPI


Board: 2 copper layers, 29.0 x 41.0 mm, 24 parts (0 on the bottom side), 20 nets.

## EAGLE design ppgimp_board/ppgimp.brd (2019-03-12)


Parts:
D1: 1N457; DIODE_THRU
J1: VDD; 1X02
J2: GND; 1X02
J3: SPI; 1X04
J4: I_Test; 1X02
J5: R_test; 1X02
R1: POT-3PIN
U1: LM334Z/NOPB; Z03A
U2: AD8400ARZ1; R_8
U3, U4: AD8400ARZ10; R_8

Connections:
1KCS: J3.3, U2.3 (!)
10KCS: J3.4, U3.3 (!CS), U4.3 (!CS)
A1: J5.1, U4.8 (A1)
GND: J2.1, J2.2, J4.2, U2.2 (GND), U3.2 (GND), U4.2 (GND); also elsewhere on the board
I_OUT: D1.2 (N), R1.2, U3.7 (W1)
MOSI: J3.2, U2.4 (SDI), U3.4 (SDI), U4.4 (SDI)
unnamed: J4.1, R1.3
R: U1.2 (R), U2.8 (A1), U3.8 (A1)
SCLK: J3.1, U2.5 (CLK), U3.5 (CLK), U4.5 (CLK)
V-: D1.1, U1.3 (V-), U2.7 (W1)
VDD: J1.1, J1.2, U1.1 (V+), U2.6 (VDD), U3.6 (VDD), U4.6 (VDD); also elsewhere on the board
W1: J5.2, U4.7 (W1)


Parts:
C1, C5: 0.1uF; 0603-CAP
C2, C6: 10uF; 0603-CAP
C3, C4: 1uF; 0603-CAP
FB1: FERRITE; 0603-FERR
J6: I2C; 1X02
J7: SEL; 1X02
R2, R3: 10K; R0603
R4: 510K; R0603
R5: 200K; R0603
R6: 100K; R0603
RFB: 1M; R0603
U5: AD5933; RS_16
U6: ADG1609; RU_16

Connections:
AGND: FB1.1, U5.13 (AGND1), U5.14 (AGND2)
GND: C1.1, C2.1, C5.1, C6.1, FB1.2, U5.12 (DGND), U6.3 (VSS), U6.15 (GND); also elsewhere on the board
unnamed: RFB.2, U5.4 (RFB)
unnamed: J7.1, U6.16 (A1)
unnamed: J7.2, U6.1 (A0)
unnamed: R4.2, U6.4 (S1A)
unnamed: R4.1, U6.13 (S1B)
unnamed: R5.2, U6.5 (S2A)
unnamed: R5.1, U6.12 (S2B)
unnamed: C3.1, U6.6 (S3A)
unnamed: C3.2, U6.11 (S3B)
unnamed: C4.1, R6.1, U6.7 (S4A)
unnamed: C4.2, R6.2, U6.10 (S4B)
SCL: J6.2, R3.1, U5.16 (SCL)
SDA: J6.1, R2.1, U5.15 (SDA)
VDD: C1.2, C2.2, C5.2, C6.2, R2.2, R3.2, U5.9 (DVDD), U5.10 (AVDD1), U5.11 (AVDD2), U6.2 (EN), U6.14 (VDD); also elsewhere on the board
VIN: RFB.1, U5.5 (VIN), U6.8 (DA)
VOUT: U5.6 (VOUT), U6.9 (DB)


Board: 2 copper layers, 32.5 x 29.0 mm, 28 parts (0 on the bottom side), 28 nets.

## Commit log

2019-02-22 update current stuff
2019-02-23 start working on the board
    [ppgimp.sch]
2019-02-24 get current source testing done
    [ppgimp.brd, ppgimp.sch]
2019-02-26 do more research hook up ad5399
    [ppgimp.brd, ppgimp.sch]
2019-03-01 finish up test board
    [ppgimp.brd, ppgimp.sch]
2019-03-12 finalize prototype
    [ppgimp.brd, ppgimp.sch]
2019-05-13 rename board
    [ppgimp.brd, ppgimp.sch]
2019-05-13 get current source code working
2019-09-04 start oximeter board
    [ppg_array_wireless.brd, ppg_array_wireless.sch, ppg_array_wireless.xlsx]
2019-09-19 big boi commit
    [electrode.brd, electrode.sch, nextflex.brd, nextflex.sch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]
2019-09-19 send boards out for production and fix imp test code
    [electrode.brd]
2019-11-05 more nextflex progress
    [nextflex.brd, nextflex.sch, oximeter.brd, oximeter.sch]
2019-11-06 finish rev a of nextflex
    [nextflex.brd, nextflex.sch]
2019-11-06 Add bom and clp files for jcl
    [BOM_REV_A.xlsx, CPL_REV_A.xlsx, nextflex.brd, nextflex.sch]
2019-11-18 Fix reads and push pull - leds light up and doesnt get hot but stil no data
2019-12-01 update firmware for electrodes and ox
2019-12-02 small fixes for anode cathone config
    [nextflex.brd, nextflex.sch]
2019-12-03 Start final revision
    [BOM_REV_A.xlsx, BOM_REV_B.xlsx, CPL_REV_A.xlsx, CPL_REV_B.xlsx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]
2019-12-03 more work on firmware, electrodes work
    [BOM_REV_B.xlsx, CPL_REV_B.xlsx]
2019-12-03 fix cs pin for mippe 32u4
2019-12-05 place final revision order for next flex
    [BOM_REV_B.xlsx, nextflex_revb.brd]
